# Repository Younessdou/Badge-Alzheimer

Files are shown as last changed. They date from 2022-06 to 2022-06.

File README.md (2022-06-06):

# Badge-Alzheimer
Projet électronique du semestre 5


# Sommaire 
### Introduction
### I) Cahier des charges
### II) Gantt et diagramme d'architecture
### III) Choix des composants
##### A) Module GPS
##### B) Module Lora
##### C) Microprocesseur
### IV) Réalisation du PCB
##### A) Choix des pins du microP
##### B) Schématic & board
##### C) Soudage des composants sur la carte
### V) Codage du module GPS 
### VI) LoRa
### VII) Alimentation
### Conclusion

# Remerciement
Nous remercions nos tuteurs durant ce projet Mr.Papazoglou et Mme.Giannini pour leurs conseils et astuces qui nous ont permis de découvrir de nouvelles choses et acquérir de nouvelles compétences tout en appliquant ce que nous avions vu durant cette année d'étude, et nous tenons aussi à remercier Mme. Kittel du bureau technique qui nous a aidé pour notre PCB.
# Introduction
Dans le cadre des projets tutorés du semestre 6, nous avons été amenés à travailler sur la conception d’un badge Alzheimer qu’on a choisi de le nommer «TrackNanny».
TrackNanny est tout simplement un outil de localisation et de prévention, destiné aux personnes atteintes d’Alzheimer ou aux personnes qu’on ne souhaiterait pas perdre à l’extérieur. Ce badge permet d’envoyer une alerte à la personne qui prend en charge l’utilisateur dès que ce dernier dépasse un rayon prédéfini par rapport à un épicentre qui est aussi prédéfini. Ce badge contient aussi un bouton SOS qui permet d’envoyer un autre message d’alerte avec la position exacte de l’utilisateur si quelqu’un l’a trouvé.
Pour notre projet on a pris l'adresse de l'ENSEA comme épicentre et on a défini un rayon de 700m.       
    <p align="center">
  
### Gantt & diagramme d’architecture
Durant ces 11 séances de projets, nous avons commencé par répartir les tâches entres nous en remplissant notre diagramme de Gantt où on a placé nos missions par ordre de priorité.

 Gantt
Et on a structuré notre projet selon le diagramme d'architecture suivant:
  
  

# I) Cahier des charges
Pendant la première séance nous avons commencé par établir un cahier des charges sur lequel on s'est basé pour la suite du projet:
    <p align="center">
  
      
    Budget: 50€
# III) Choix des composants
### A) Module GPS
      Module GPS : SKU:TEL0132




  
 ### B) Module LORA
   Module LoRa-E5 Grove 113020091\
      

      
On a choisi le module LoRa-E5 Grove 113020091 puisque c'était le moins cher et le plus compacte par rapport aux autres.
  
 ### C) Microprocesseur
     STM32L412KBT6


      
tableau des microprocesseurs proposés:



  Au début on avait le choix entre 4 microprocesseurs, et puisqu’on va utiliser 2 UART et 1 GPIO; 1 pour le module GPS et 1 pour le LoRa, donc il nous restait 2 choix et puisque le STM32L021K4T6 n'est pas toujours fiable , on a opté pour le 4ème vu son prix qui est presque la moitié du 3ème et aussi puisqu’il a le même package que les autres donc on aura la possibilité de le changer sur notre PCB et aussi puisqu’il contient que 32 pin et ça reste plus simple et facile à souder et manipuler que celui avec 64 pins.

# IV) Réalisation du PCB
        
 ### A) Choix des pins du microP
Nous avons fait bon usage du Logiciel STM32CubeIDE afin de voir les pins associés à l’UART, leurs numéros ainsi que leurs dispositions lors de la création de la carte Pcb.
Après ajout des pins pour notre bouton SOS et RESET, on se retrouve avec une Pin view comme ci-contre :


- Pin PA2-3 : Module GPS
- Pin PA5 : Bouton SOS
- Pin PA14-15 : RESET 
- Pin PA9-10 : Module LoRaWan   
        
 ### B) Schematic et board
 
 Nous avons commencé par créer notre PCB sur eagle en téléchargeant les librairies contenant nos composants, puis on a créé notre schématic qui contient la partie microP, l'alimentation les connecteurs pour le module GPS et LoRa ainsi que nos deux boutons reset et SOS.
        
 

  À partir de ce schématic on a généré notre board pour relier les composants entre eux en top ou en buttom.
        
 

  Après le routage de ce dernier, on a bien respecté notre objectif qui est de réduire l'espace entre les composants et mettre un grand nombre de liaison en top afin d'obtenir une carte adéquate avec la forme de notre badge, ensuite on l'a imprimé et on a soudé les composants dessus à l'aide de mr.Papazouglou et mme.Kittel.
 
 Voici le format final de notre PCB:
        


 # V) Codage du module GPS
 Cette partie a été faite par deux autres étudiants; Alexis Regnault et Valérian PRIOU qui se sont occupés de la partie software de plusieurs projets dont le nôtre, veuillez trouver leurs rapports pour notre projet ci-joint avec les fichiers, il est intitulé «Rapport_Alzheimer_PRIOU_REGNAULT.pdf» ainsi que le git du codage du module GPS via le lien ci-dessous.
https://github.com/ValerianPRIOU/Alzheimer
        
 # VI) LoRa or LoRaWAN?
 Cette partie a été géré par deux autres étudiants; Mohamed Amine Bouhyat Oliver BELLIARD ABREU, ils ont aussi travaillé sur la partie LoRawan des autres projets. Veuillez trouver le lien de leurs git ci-dessous.
        
  https://github.com/OliverBELLIARD/LoRaWAN     

 # VII) Alimentation:
 Cette partie a été géré par deux étudiantes; Inass Rachidi Manon COTTAR qui s'occupaient de l'alimentation de plusieurs projets en même temps, vous trouverez le lien ci-dessous du travail détaillé qui a été fait en parallèle avec nous.

https://github.com/inassra/batterie

# Conclusion
Pour le moment, nous n'avons toujours pas terminé notre projet, il nous reste dans la partie software l'assemblage du code du module GPS et le module LoRa dans un seul code qui doit être implémenter par la suite dans le microprocesseur, lors du test de notre carte on a eu un problème avec le régulateur qui délivre les 5V en revanche on obtient bien nos 6V à l'entrée ainsi que nos 3,3V à la sortie de l'autre régulateur. Ce premier projet a été très intéressant puisqu'on a pu appliquer la plupart des connaissances et compétences vu durant cette année. L'idée du projet est très intéressante et on peut poursuivre le travail sur ce projet après en essayant de le compléter et de l'améliorer en modifiant notre cahier des charges et en ajoutant d'autres missions comme un accéléromètre pour détecter la chute de l'utilisateur.

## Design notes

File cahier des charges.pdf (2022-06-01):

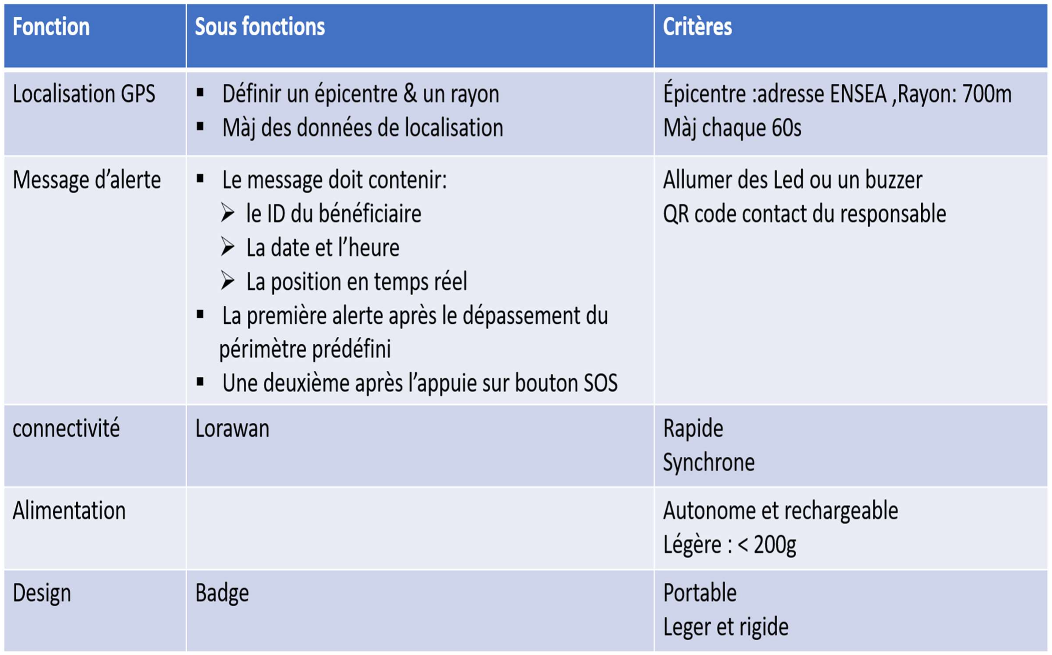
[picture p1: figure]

Budget :50 €
Date de remise : Fichier PCB => 17/05/2022 PCB complet => 24 /05/2022
Présentation finale et démonstration 01/06/2022

# Cahier des charges

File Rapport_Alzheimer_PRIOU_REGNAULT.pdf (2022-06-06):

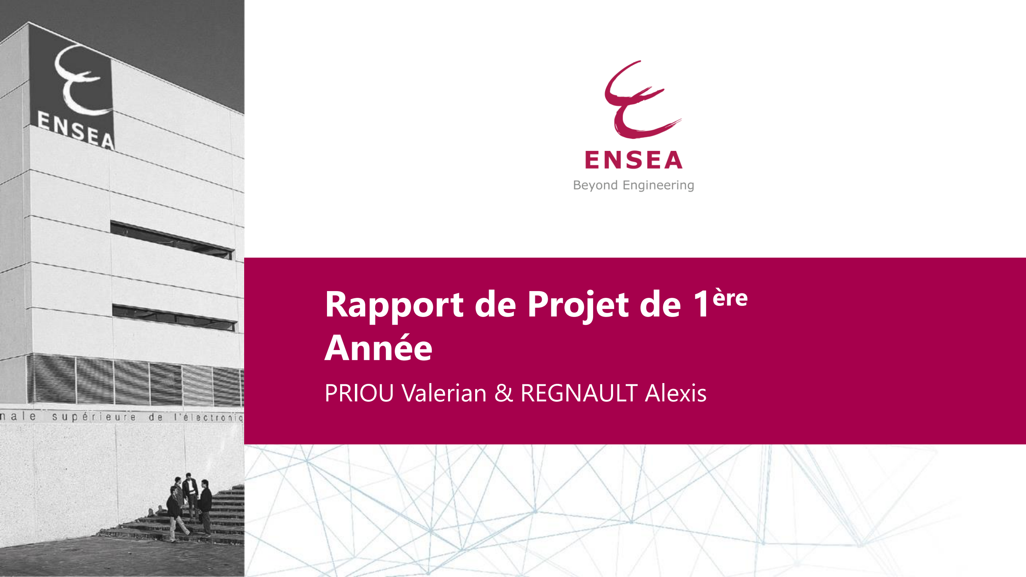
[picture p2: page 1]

# Rapport de Projet de 1ère Année

### PRIOU Valerian & REGNAULT Alexis

Prénom NOM - Date

# Le projet :

Badge Alzheimer

Notre objectif : Permettre de savoir si la personne en possession du badge est trop éloignée grâce à un GPS et si oui, pouvoir récupérer ses coordonnées GPS.

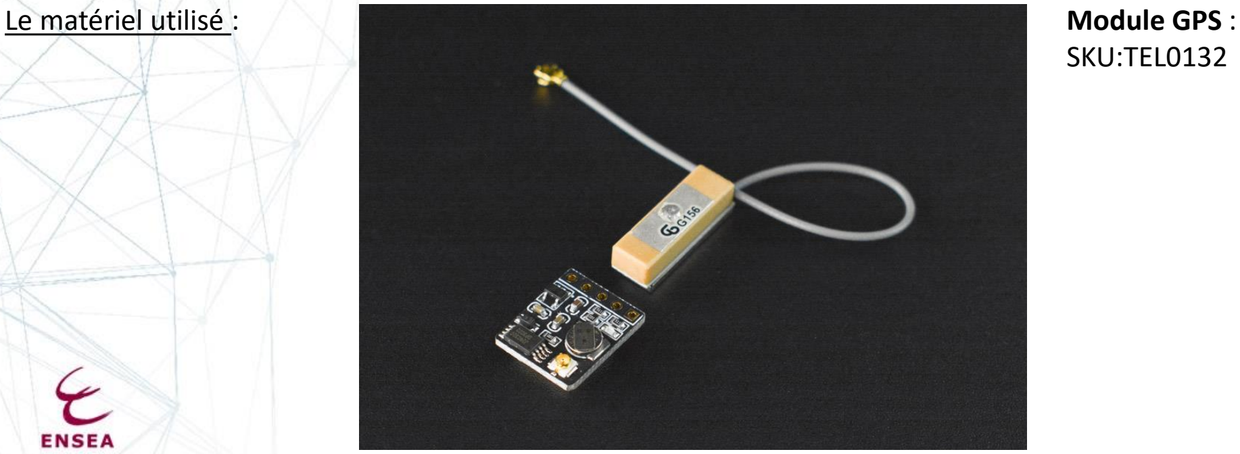
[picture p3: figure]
Le matériel utilisé :; Module GPS :; SKU:TEL0132

# Choix des capteurs :

Prix : • GPS : 15.05 €/u

Taille : Le module est assez petit, ce qui est nécessaire au vu du cahier des charges

Data Sheet : • GPS : https://wiki.dfrobot.com/GPS_+_BDS_BeiDou_Dual_Module_SKU_TEL0132

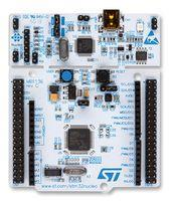
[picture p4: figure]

Carte de test : STM32F410 Nucleo-64

# Branchement de la carte STM32 :

Badge Alzheimer

Module GPS :

- VCC : 5V
- GND : GND
- RX (GPS) : TX (Carte) PA9 (D10)
- TX (GPS) : RX (Carte) PA10 (D2)

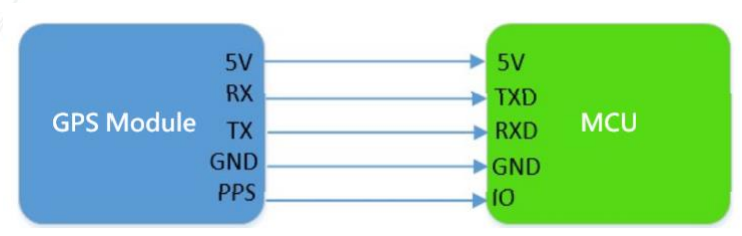
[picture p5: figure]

# Notre Code :

## Lien GitHub :

Badge Alzheimer

https://github.com/ValerianPRIOU/Alzheimer

# Les difficultés rencontrées :

Nous avons rencontré plusieurs difficultés lors de ce projet pour la gestion du module GPS, il a déjà fallu acquérir les trames du GPS, sur conseil de notre professeur nous les avons ensuite synchronisées. Viens alors le plus gros problème : récupérer les informations qui nous intéressaient dans des chaînes de caractères, pour réussir nous avons du repenser notre code de manière plus logique et compréhensible. Ensuite nous avons du convertir ces chaînes de caractères en flottants pour pouvoir exploiter les coordonnées de latitude et de longitude. Enfin grâce à une simple formule de distance normée au carré nous avons pu établir un rayon dans lequel la personne peut se déplacer. Au-delà de ce périmètre nous recevons sur le terminal les coordonnées de la personne. Pour améliorer le projet, il faudrait transmettre ces coordonnées avec le LoraWan, nous aurions également aimer avoir le temps de reprendre le code en le divisant avec des fonctions pour le rentre plus compréhensible, coder un bouton « Reset » et pouvoir changer facilement la position de référence (point de départ de la

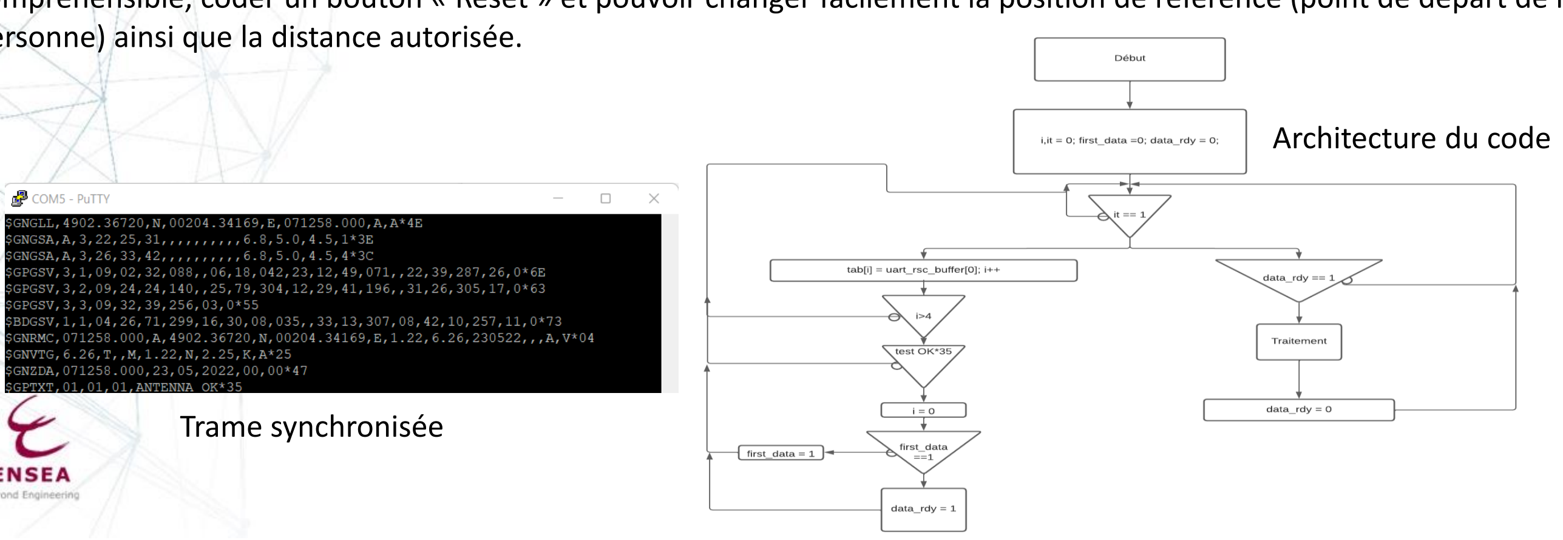
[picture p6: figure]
Trame synchronisée; Architecture du code

personne) ainsi que la distance autorisée.

# Ce que nous a apporté les projets :

Ces projets nous ont permis de développer à la fois des « Hard Skills » et des « Soft Skills » en effet nous avons appris à souder, à utiliser STM32CubeIDE pour coder des capteurs avec des communications UART, ce qui nous a permis d’appliquer nos cours de Microprocesseurs (gestion de registres, interruptions, concaténations) tout en revoyant le langage C.
Mais ces projets nous ont également permis de développer nos compétences en gestion de projet notamment par leur aspect transverse ainsi que notre communication avec des personnes que nous ne connaissions pas.
Notre groupe (composé de 2 membres qui ne se connaissaient pas avant) en est le parfait exemple, Valérian (1B) et Alexis (1A).
Nous avons également appris malgré nous la rapidité à laquelle les deadlines peuvent arriver et à revoir le cahier des charges et les priorités en conséquence.
Finalement, ce projet de 1ère année aura été une bonne expérience et il nous permettra d’aborder sereinement le projet de 2ème année (qui aura ses difficultés sans aucun doute).

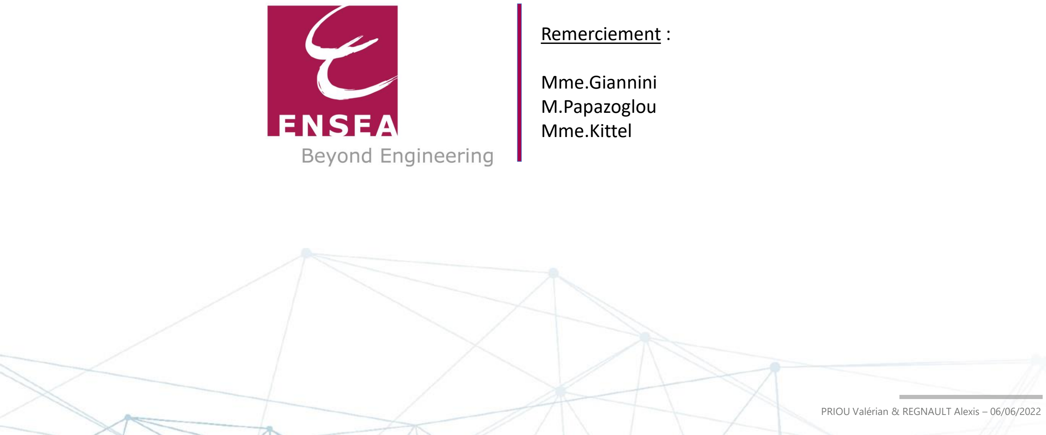
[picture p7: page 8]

PRIOU Valérian & REGNAULT Alexis – 06/06/2022

Remerciement :

Mme.Giannini
M.Papazoglou
Mme.Kittel

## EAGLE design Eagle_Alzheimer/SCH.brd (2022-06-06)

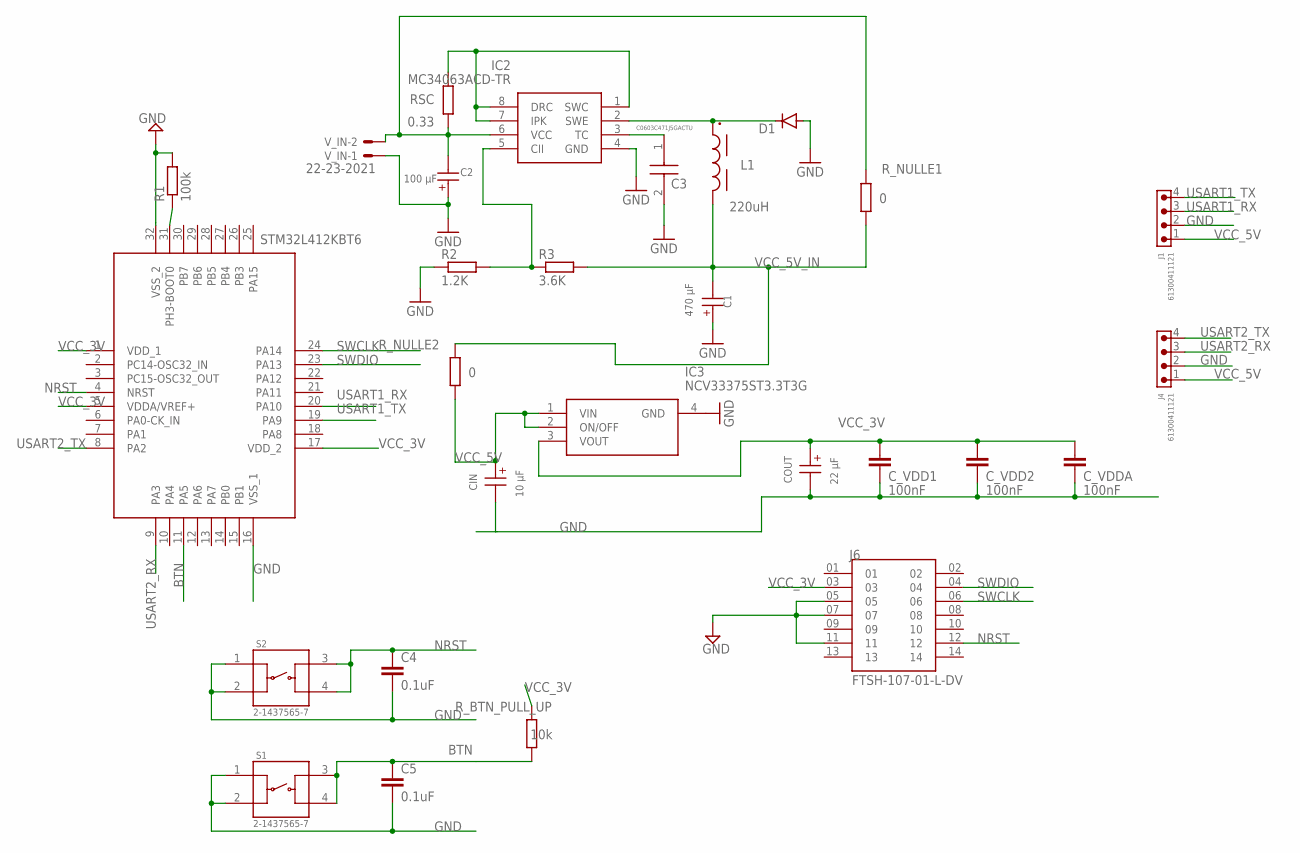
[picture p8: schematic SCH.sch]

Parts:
C1: 470 µF; WCAP-ASLL_8X10.5(DXL)
C2: 100 µF; WCAP-ASLL_6.3X7.7(DXL)
C3: C0603C471J5GACTU; C0603
C4, C5: 0.1uF; C0603
CIN: 10 µF; WCAP-ASLL_4X5.5(DXL)
COUT: 22 µF; WCAP-ASLL_5X5.5(DXL)
C_VDD1, C_VDD2: 100nF; C0603
C_VDDA: 100nF; C0603
D1: DIODE-DO214AC; DO214AC
IC1: STM32L412KBT6; QFP80P900X900X160-32N
IC2: MC34063ACD-TR; SOIC127P600X175-8N
IC3: NCV33375ST3.3T3G; SOT230P700X175-4N
J1, J4: 61300411121
J6: FTSH-107-01-L-DV; SAMTEC_FTSH-107-01-L-DV
L1: 220uH; WE-PDA_1260
R1: 100k; R0603
R2: 1.2K; R0603
R3: 3.6K; R0603
RSC: 0.33; R1206W
R_BTN_PULL_UP: 10k; R0603
R_NULLE1, R_NULLE2: 0; R0603
S1, S2: 2-1437565-7; SW_2-1437565-7
V_IN: 22-23-2021

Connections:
BTN: C5.1, IC1.11 (PA5), R_BTN_PULL_UP.1, S1.3, S1.4
GND: C1.1 (+), C2.1 (+), C3.2, C4.2, C5.2, CIN.2 (-), COUT.2 (-), C_VDD1.2, C_VDD2.2, C_VDDA.2, D1.A, IC1.16 (VSS_1), IC1.32 (VSS_2), IC2.4 (GND), IC3.4 (GND), J1.2, J4.2, J6.05, J6.07, J6.11, R1.2, R2.1, S1.1, S1.2, S2.1, S2.2, V_IN.1
unnamed: IC1.31 (PH3-BOOT0), R1.1
unnamed: IC2.1 (SWC), IC2.7 (IPK), IC2.8 (DRC), RSC.2
unnamed: IC2.5 (CII), R2.2, R3.1
unnamed: C3.1, IC2.3 (TC)
unnamed: D1.C, IC2.2 (SWE), L1.1
NRST: C4.1, IC1.4 (NRST), J6.12, S2.3, S2.4
SWCLK: IC1.24 (PA14), J6.06
SWDIO: IC1.23 (PA13), J6.04
USART1_RX: IC1.20 (PA10), J1.3
USART1_TX: IC1.19 (PA9), J1.4
USART2_RX: IC1.9 (PA3), J4.3
USART2_TX: IC1.8 (PA2), J4.4
VCC_3V: COUT.1 (+), C_VDD1.1, C_VDD2.1, C_VDDA.1, IC1.1 (VDD_1), IC1.5 (VDDA/VREF+), IC1.17 (VDD_2), IC3.3 (VOUT), J6.03, R_BTN_PULL_UP.2
VCC_5V: CIN.1 (+), IC3.1 (VIN), IC3.2 (ON/OFF), J1.1, J4.1, R_NULLE2.1
VCC_5V_IN: C1.2 (-), L1.2, R3.2, R_NULLE1.1, R_NULLE2.2
VCC_6V: C2.2 (-), IC2.6 (VCC), RSC.1, R_NULLE1.2, V_IN.2

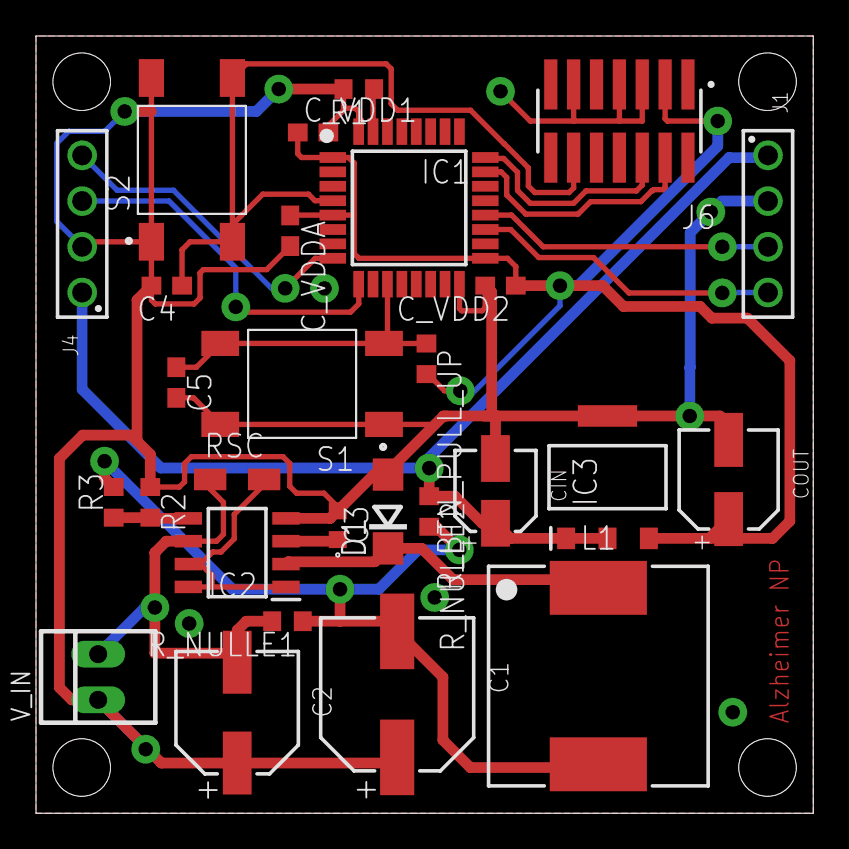
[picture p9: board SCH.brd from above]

Board: 2 copper layers, 43.2 x 43.2 mm, 28 parts (0 on the bottom side), 18 nets.

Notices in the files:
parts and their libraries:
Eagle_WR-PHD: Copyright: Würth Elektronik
